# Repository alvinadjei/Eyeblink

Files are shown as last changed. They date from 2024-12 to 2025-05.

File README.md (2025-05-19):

# Eyeblink Experiment

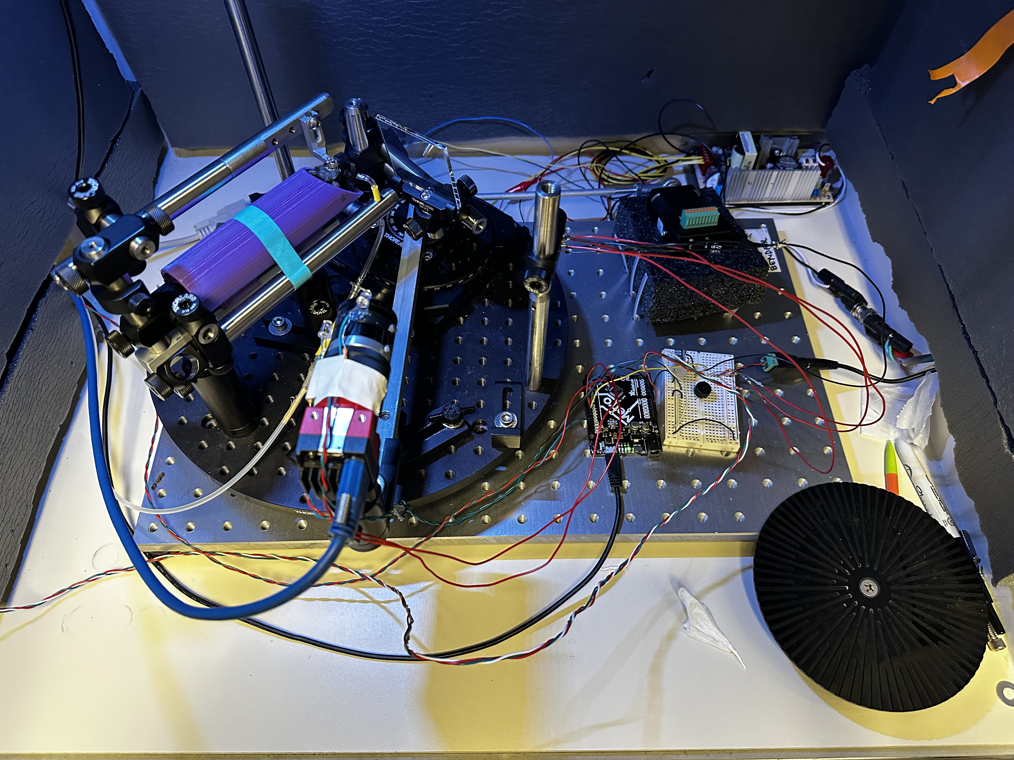
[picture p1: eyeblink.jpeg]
Eyeblink setup


This repository contains code and instructions for setting up an eyeblink conditioning experiment in mice. In this case, the conditioned stimulus is a short musical tone, 
and the unconditioned stimulus is a short puff of air to the mouse's eye. An infrared camera records a live feed of the mouse's eye, sending each frame to a Python script
that calculates how open or closed the mouse's eye is every millisecond.

This page is a work in progress, and will be updated as the project progresses.

Author(s): Alvin Adjei, University of California San Francisco

## Requirements
### Hardware
- Designed to work on Windows 10 and newer. Untested on Mac.
- 1 $\times$
  <a href="https://store.arduino.cc/products/arduino-uno-rev3?srsltid=AfmBOophdIvm8RfX5799wr4zovlr1sxV1jH-H7QClWuCym0v6gZN2AgC">
    Arduino Uno
  </a>
  or similar microcontroller (we used an <a href="https://www.adafruit.com/product/2488">Adafruit Metro Board</a>)
- 1 $\times$ Picospritzer III or similar device that can accept Arduino HIGH as input signal and outputs an air puff
- 1 $\times$
  <a href="https://www.adafruit.com/product/1426">
    neopixel strip
  </a>
- 5 $\times$ infrared LEDs (the ones we used emit light w/ 850nm wavelength)
- 5 $\times$ 220 $\Omega$ resistors
- 1 $\times$ N-Channel MOSFET
- 1 $\times$ passive piezoeelectric buzzer
- 1 $\times$
  <a href="https://www.edmundoptics.com/p/allied-vision-alvium-1800-u-120m-13-12mp-c-mount-usb-31-monochrome-camera/48262/">
    Allied Vision Alvium 1800 U-120m Monochrome Camera</a>,
  or similar camera with ___no___ infrared filter and compatible lens (in this case, for a 1/3" sensor)
  - Camera drivers and software are <a href="https://www.alliedvision.com/en/products/software/" target="_blank">here</a>
  - Python API manual is <a href="https://docs.alliedvision.com/Vimba_X/Vimba_X_DeveloperGuide/pythonAPIManual.html">here</a>
- 1 $\times$ <a href="https://www.edmundoptics.com/p/m6-and--20-mounting-plate-for-alvium/42353/">M6 and ¼-20 Mounting Plate for Alvium</a>
- 1 $\times$ Infrared mirror
- Other materials shown in the image at the top come from Thorlabs

### Software
The code for this project is written in Python and in the Arduino IDE. The required Python libraries and their versions are specified in <code>requirements.txt</code>.
To install them, run <code>python -m pip install -r requirements.txt</code>
in the terminal in the project's root directory.

The Arduino code requires the Adafruit NeoPixel library, which can be installed via the Library Manager in the Arduino IDE.

To interface with the camera, install the <a href="https://www.alliedvision.com/en/products/software/vimba-x-sdk/">Vimba X SDK</a> and the
<a href="https://docs.alliedvision.com/Vimba_X/Vimba_X_DeveloperGuide/about.html#installation">USB driver</a>. Then,
follow the instructions found <a href="https://docs.alliedvision.com/Vimba_X/Vimba_X_DeveloperGuide/pythonAPIManual.html">here</a> to install
Vimba X's Python API, VmbPy.

## Assembly
<figure>
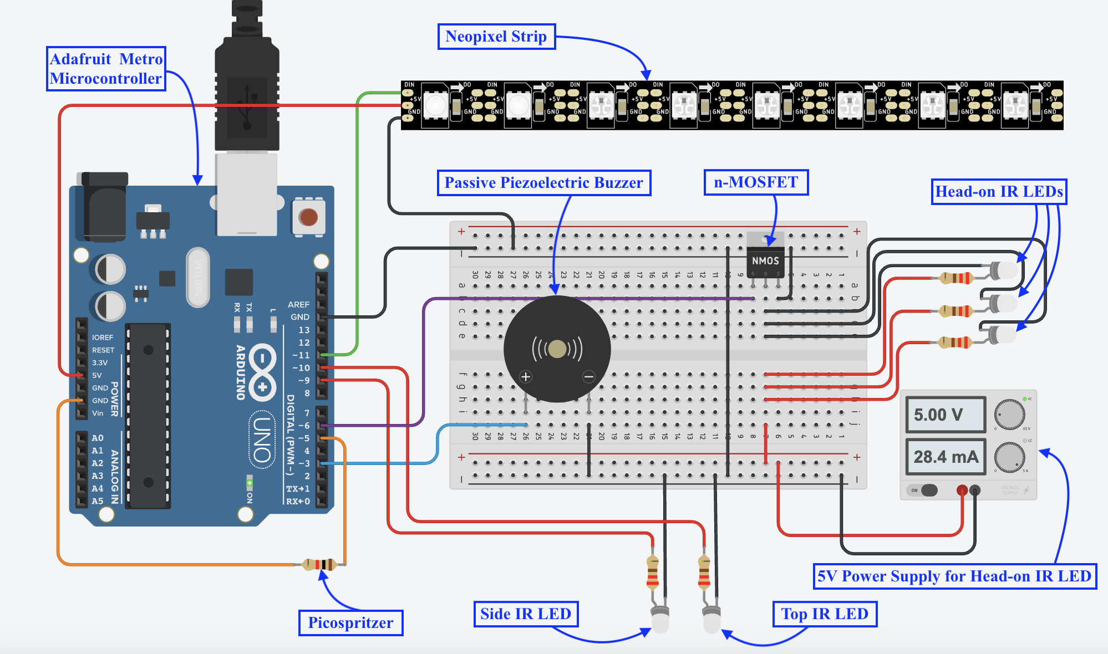
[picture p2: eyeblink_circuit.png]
Circuit Diagram
  
  <figcaption>
    Circuit diagram.
    <p>
      <b>Note: The Adafruit NeoPixel library uses pin 11 as the default data output pin for Neopixels on Arduino boards. If using an Adafruit Metro board like we did, pin 6 is the default data output pin for the Neopixels. Make sure your circuit and code align with the board you are using by appropriately setting the <i>PIX_PIN</i> and <i>IR_LED_3</i> variables in <code>Code/capture/Arduino/serial_control/serial_control.ino</code> according to your hardware.
      </b>
    </p>
    <p>
      The resistor in the bottom left represents the Picospritzer. The "Side IR LED" and "Top IR LED" are attached
      to the left and top of the camera. The "Head-on IR LEDS" are attached to a post facing the mouse head-on.
    </p>
  </figcaption>
</figure>

## Run Experiment

<ol>
  <li>Clone or download this repository.</li>
  <li>Plug USB camera and Arduino Uno into USB ports in the computer. The camera needs to be plugged into a USB 3 port, which is usually identified by having the color blue on the inside.</li>
  <li> Open <code>Code/capture/Arduino/serial_control/serial_control.ino</code>. This file contains instructions for the Arduino to execute when it receives serial instructions. Here, you can adjust constants like <code>csDuration</code> (how long the tone plays), <code>ISI</code> (inter-stimulus interval), and <code>usDuration</code> (how long the airpuff lasts) to your liking. Then, upload the code to the Arduino.</li>
  <li>Open <code>Code/capture/run_experiment.py</code></li>
  <li>Open the Device Manager on Windows to determine which USB port the camera is plugged into (e.g. 'COM4'), and set the <code>arduino_port</code>
  variable equal to this name (we have set this variable to <code>'COM4'</code> by default)</li>
  <li>
    Adjust global constants like <code>num_trials</code> (number of trials in an experiment) and <code>ITI</code> (inter-trial interval)
    to your liking.
  </li>
  <li>Navigate to the root directory of this project in the terminal, activate the <code>.venv-wind</code> virtual environment, then press the run button in your code editor to run the script.</li>
  <li>In the terminal, you will be prompted to enter the mouse's ID. Enter an ID of your choice and press Enter.</li>
  <li>Next, you will be asked if this is the first recording of the day for this mouse. If you enter 'y' for yes, you will continue to the next steps where you can run the experiment for <code>num_trials</code> iterations. If you enter 'n' for no, you will then be asked how many trials you would like to run on the mouse. Once you enter this, the following steps will be the same.</li>
  <li>
    Now, the GUI will open. If the window doesn't appear, check the app taskbar/dock for a new app running. The window should look something like this:
    <p>
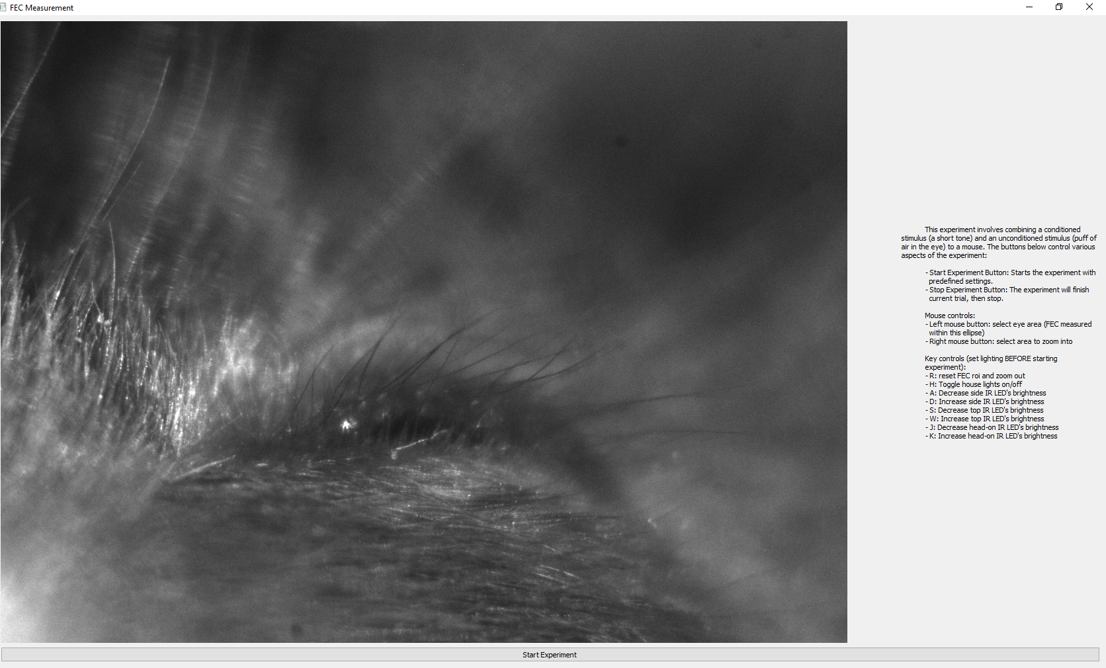
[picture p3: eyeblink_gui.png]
Eyeblink gui
      
    </p>
    <p>
      On the left, you should see a live video feed from the USB camera. On the right, there are instructions on how to adjust the brightness of the
    infrared LEDs, zoom in to the image, and select the region of interest (ROI) containing the mouse's eye. Once an ROI has been selected, click 
    "Start Experiment" at the bottom to begin data acquisition.
    </p>
  </li>
  <li>
    The experiment will run for the number of trials that you specified in <code>num_trials</code>. At any point, click the "Stop Experiment" button to
  terminate the experiment. If you terminate early, the data from the experiment up to that point will still be saved to CSV files.
  </li>
  <li>
    When the experiment is over, the data will be saved to two CSV files in the <code>Data/</code> directory. Each file will have the timestamp when it was
    saved in its name. The CSV saved to <code>Data/FEC/{mouse_id}/</code> has three columns: "Timestamp", "Trial #", and "FEC". It contains the timestamp, trial number, and
    fraction of eye closure, or FEC, in each frame. The CSV saved to <code>Data/stim/{mouse_id}/</code> has three columns: "Trial #", "CS Timestamp", and "Airpuff" containing the timestamp
    at which each trial's conditioned stimulus (in our case, the tone that plays before the airpuff) begins and whether an unconditioned stimulus (air puff) was executed during that trial.
  </li>
</ol>

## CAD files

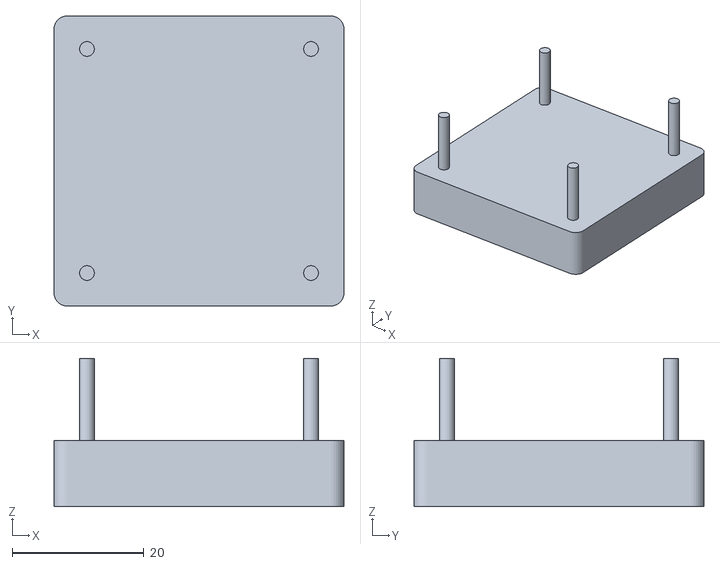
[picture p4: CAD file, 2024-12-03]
Camera Holder/ir_camera_holder.stl
44.0 x 44.0 x 22.5

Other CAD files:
Archived/Camera Holder/ir_camera_holder.f3d
Camera Holder/ir_camera_holder.f3d

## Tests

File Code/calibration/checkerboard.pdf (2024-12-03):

10/17/24, 2:56 PM | Checkerboard-A4-30mm-8x6.svg
file:///Users/alvinadjei/Desktop/UCSF/Bender Lab/VOR/Design/IR Camera/Checkerboard-A4-30mm-8x6.svg | 1/1

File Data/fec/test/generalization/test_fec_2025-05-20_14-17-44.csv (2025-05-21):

Timestamp | Trial # | FEC
2025-05-20 14:18:10.031412 | 1 | 0
2025-05-20 14:18:10.081845 | 1 | 0
2025-05-20 14:18:10.131754 | 1 | 0
2025-05-20 14:18:10.164043 | 1 | 0
2025-05-20 14:18:10.210908 | 1 | 0
2025-05-20 14:18:10.257772 | 1 | 0
2025-05-20 14:18:10.304635 | 1 | 0
2025-05-20 14:18:10.335880 | 1 | 0
2025-05-20 14:18:10.390175 | 1 | 0
2025-05-20 14:18:10.437007 | 1 | 0
2025-05-20 14:18:10.468280 | 1 | 0
2025-05-20 14:18:10.515151 | 1 | 0
2025-05-20 14:18:10.562011 | 1 | 0
2025-05-20 14:18:10.597852 | 1 | 0
2025-05-20 14:18:10.644746 | 1 | 0
2025-05-20 14:18:10.691609 | 1 | 0
2025-05-20 14:18:10.738475 | 1 | 0
2025-05-20 14:18:10.785309 | 1 | 0
2025-05-20 14:18:10.816591 | 1 | 0
2025-05-20 14:18:10.875238 | 1 | 0
2025-05-20 14:18:10.919471 | 1 | 0
2025-05-20 14:18:10.961386 | 1 | 0
2025-05-20 14:18:11.007236 | 1 | 0
2025-05-20 14:18:11.050125 | 1 | 0
2025-05-20 14:18:11.093006 | 1 | 0
2025-05-20 14:18:11.137887 | 1 | 0
2025-05-20 14:18:11.180771 | 1 | 0
2025-05-20 14:18:11.220816 | 1 | 0
2025-05-20 14:18:11.267677 | 1 | 0
2025-05-20 14:18:11.298896 | 1 | 0
2025-05-20 14:18:11.349378 | 1 | 0
2025-05-20 14:18:11.399887 | 1 | 0
2025-05-20 14:18:11.433147 | 1 | 0
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

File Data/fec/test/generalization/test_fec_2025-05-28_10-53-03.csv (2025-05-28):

Timestamp | Trial # | FEC
2025-05-28 10:57:31.168501 | 1 | 0
2025-05-28 10:57:31.198435 | 1 | 0
2025-05-28 10:57:31.248202 | 1 | 0
2025-05-28 10:57:31.295067 | 1 | 0
2025-05-28 10:57:31.341963 | 1 | 0
2025-05-28 10:57:31.373202 | 1 | 0
2025-05-28 10:57:31.420069 | 1 | 0
2025-05-28 10:57:31.466932 | 1 | 0
2025-05-28 10:57:31.513768 | 1 | 0
2025-05-28 10:57:31.560630 | 1 | 0
2025-05-28 10:57:31.591901 | 1 | 0
2025-05-28 10:57:31.641271 | 1 | 0
2025-05-28 10:57:31.691502 | 1 | 0
2025-05-28 10:57:31.730806 | 1 | 0
2025-05-28 10:57:31.780979 | 1 | 0
2025-05-28 10:57:31.814050 | 1 | 0
2025-05-28 10:57:31.866011 | 1 | 0
2025-05-28 10:57:31.911924 | 1 | 0
2025-05-28 10:57:31.947882 | 1 | 0
2025-05-28 10:57:31.994743 | 1 | 0
2025-05-28 10:57:32.041638 | 1 | 0
2025-05-28 10:57:32.072879 | 1 | 0
2025-05-28 10:57:32.119743 | 1 | 0
2025-05-28 10:57:32.166578 | 1 | 0
2025-05-28 10:57:32.213445 | 1 | 0
2025-05-28 10:57:32.260306 | 1 | 0
2025-05-28 10:57:32.291577 | 1 | 0
2025-05-28 10:57:32.349174 | 1 | 0
2025-05-28 10:57:32.381305 | 1 | 0
2025-05-28 10:57:32.431035 | 1 | 0
2025-05-28 10:57:32.480002 | 1 | 0
2025-05-28 10:57:32.514630 | 1 | 0
2025-05-28 10:57:32.564548 | 1 | 0
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

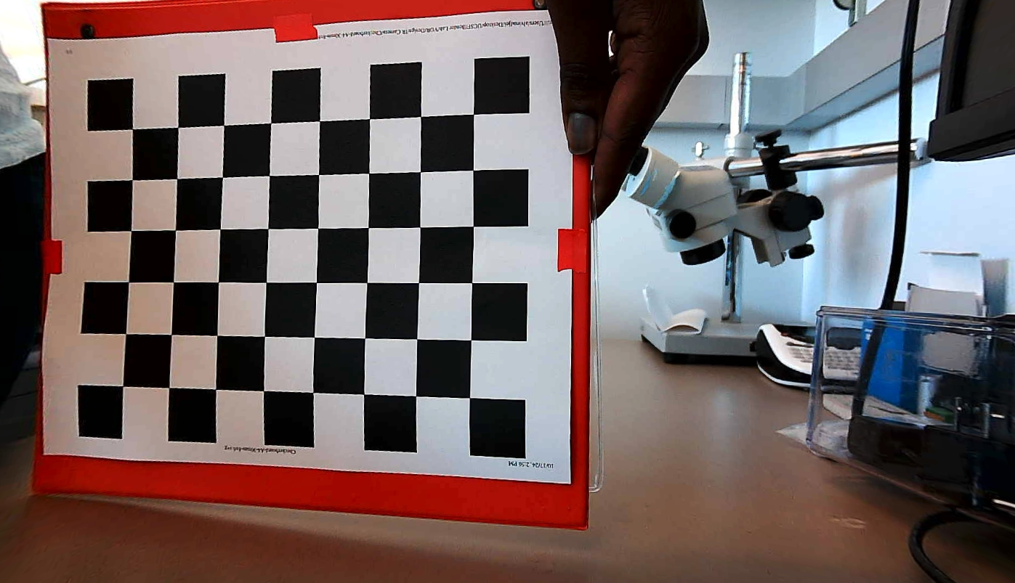
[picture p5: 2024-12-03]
Code/calibration/undistorted/calib_left12.png

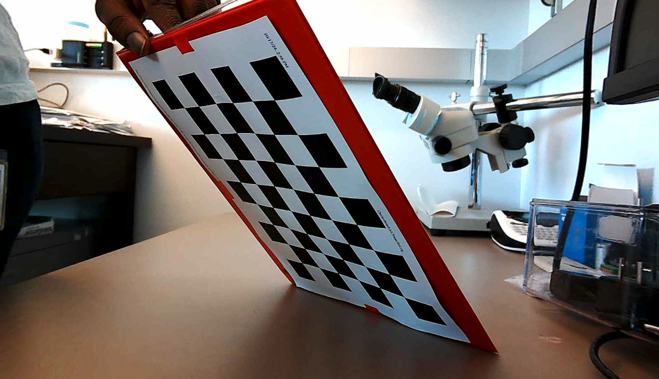
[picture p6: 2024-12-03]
Code/calibration/undistorted/calib_left10.png

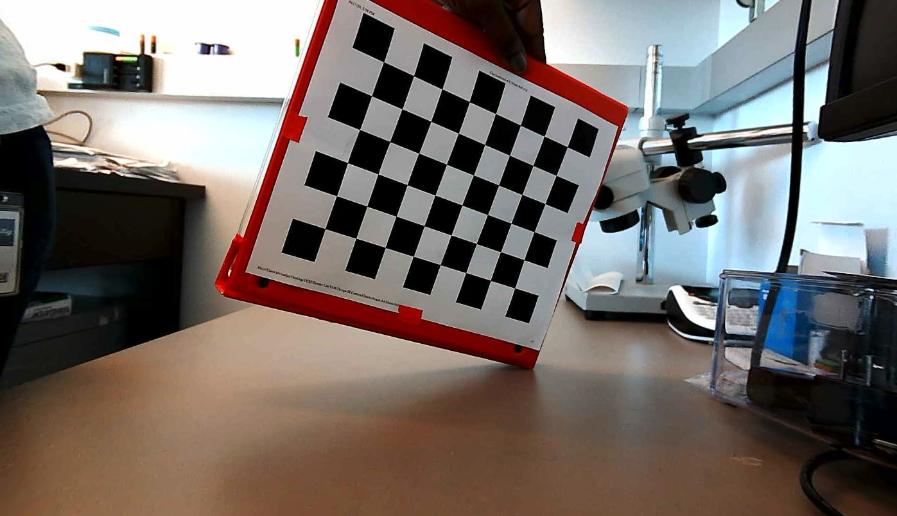
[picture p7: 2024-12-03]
Code/calibration/undistorted/calib_left05.png

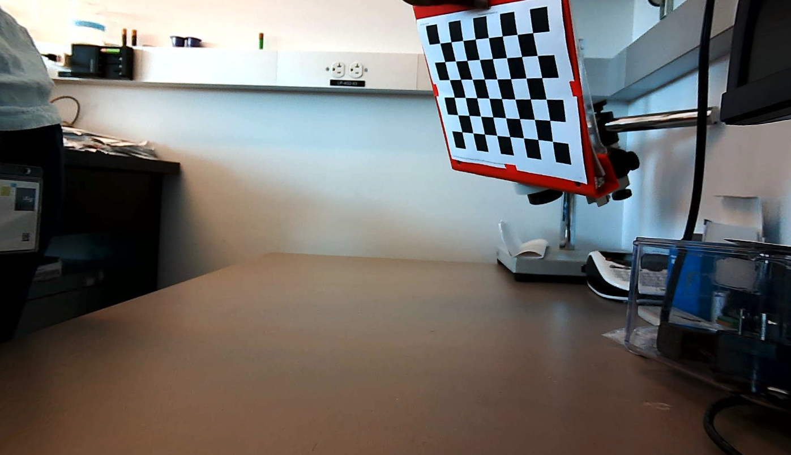
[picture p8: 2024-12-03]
Code/calibration/undistorted/calib_left01.png

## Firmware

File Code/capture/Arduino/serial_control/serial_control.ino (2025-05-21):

#include <Adafruit_NeoPixel.h>

#define BUZZER_PIN 3 // Buzzer control pin
#define PUFF_PIN 5 // Airpuff control pin
#define PIX_PIN 6 // Neopixel control pin
#define PIX_COUNT 8 // Number of NeoPixels
#define IR_LED_1 9 // Side IR LED control pin
#define IR_LED_2 10 // Top IR LED control pin
#define IR_LED_3 11 // Head-on IR LED control pin

// Define constants
int csDuration = 350; // 350 ms duration for CS
int ISI = 300; // 300 ms b/w CS onset and US onset
int usDuration = 50; // 50 ms duration for US

// Initialize Neopixel strip
Adafruit_NeoPixel strip(PIX_COUNT, PIX_PIN);

// Define NeoPixel white light color
uint32_t white = strip.Color(255, 255, 255);

// Define starting LED brightnesses
int brightness_1 = 255; // Side IR LED
int brightness_2 = 255; // Top IR LED
int brightness_3 = 255; // Head-on IR LED

// Default buzzer frequency
int freq;

// Keep track of whether neopixels are on or off
bool pixOn = true;

void setup() {
  // Setup neopixel strip
  strip.begin();
  strip.show(); // Initialize all pixels to 'off'
  
  // Initialize control pins
  pinMode(BUZZER_PIN, OUTPUT); // Buzzer
  pinMode(PUFF_PIN, OUTPUT); // Air puff

  // Initialize serial communication
  Serial.begin(9600);
}

void loop() {

  // Write brightness values to IR LED control pins
  analogWrite(IR_LED_1, brightness_1); // side
  analogWrite(IR_LED_2, brightness_2); // top
  analogWrite(IR_LED_3, brightness_3); // head-on

  // Turn overhead light on/off depending on value of pixOn
  if (pixOn) { // switch pixels on
        strip.fill(white); // Turn all pixels white
        strip.show(); // Push data to NeoPixel
        
      } else { // switch pixels off
        // Turn off all pixels
        strip.clear();
        strip.show();
      }
  
  if (Serial.available() > 0) {
    char command = Serial.read();
    
    // Command to toggle houselight
    if (command == 'h') { 
      pixOn = !pixOn; // toggle pixOn bool
      if (pixOn) {
        Serial.println("on");
      } else {
        Serial.println("off");
      }
    }

    // Command to turn down side IR brightness
    if (command == 'a') { 
      if (brightness_1 > 0) {
        brightness_1 -= 5;
        Serial.println(brightness_1);
      } else {
        Serial.println(-1);
      }
    }

    // Command to turn up side IR brightness
    if (command == 'd') { 
      if (brightness_1 < 255) {
        brightness_1 += 5;
        Serial.println(brightness_1);
      } else {
        Serial.println(-1);
      }
    }

    // Command to turn down top IR brightness
    if (command == 's') { 
      if (brightness_2 > 0) {
        brightness_2 -= 5;
        Serial.println(brightness_2);
      } else {
        Serial.println(-1);
      }
    }

    // Command to turn up top IR brightness
    if (command == 'w') { 
      if (brightness_2 < 255) {
        brightness_2 += 5;
        Serial.println(brightness_2);
      } else {
        Serial.println(-1);
      }
    }

    // Command to turn down head-on IR brightness
    if (command == 'j') { 
      if (brightness_3 > 0) {
        brightness_3 -= 5;
        Serial.println(brightness_3);
      } else {
        Serial.println(-1);
      }
    }

    // Command to turn up head-on IR brightness
    if (command == 'k') { 
      if (brightness_3 < 255) {
        brightness_3 += 5;
        Serial.println(brightness_3);
      } else {
        Serial.println(-1);
      }
    }

    // Command to run trial
    if (command == 'T' || command == 'F') {
      // Conditioned stimulus
      if (command == 'F') {
        // Wait for the rest of the int to arrive
        freq = Serial.parseInt(SKIP_NONE, 'F') * 1000;  // Reads the number after 'F'
      } else {
        freq = 10000;
      }

      // Begin CS-US
      Serial.println("d");
      tone(BUZZER_PIN, freq);
      
      delay(ISI); // Wait for ISI before starting US

      // If command is 'F', don't do airpuff
      if (command == 'T') {
        // Unconditioned stimulus
        digitalWrite(PUFF_PIN, HIGH); // Start airpuff
        delay(usDuration); // Duration of the air puff
        digitalWrite(PUFF_PIN, LOW);
      } else { // no airpuff
        delay(usDuration); // Duration of the air puff
      }

      delay(csDuration - ISI - usDuration); // Finish playing tone
      noTone(BUZZER_PIN);
    }
  }
}

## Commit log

2024-12-03 Created repo
    [ir_camera_holder.f3d, ir_camera_holder.stl, mouse_0_fec.csv, mouse_0_stim.csv]
2024-12-04 Transitioned to windows
    Need to fix camera feed dimensions and coordinates, acting funky
    [mouse_0_fec.csv, mouse_0_stim.csv]
2024-12-04 Fixed cv2 window
    Image gets laggy at the beginning of each trial when bulk of threading is happening, need to explore multiprocessing option to see if that helps
    [ir_camera_holder.f3d, ir_camera_holder.stl, mouse_0_fec.csv, mouse_0_stim.csv]
2024-12-09 Saved working threading code
2024-12-09 Fixed threading file location
2024-12-09 Arduino code for ir leds
2025-01-02 Added multiprocessing to mitigate camera lag
2025-01-03 Removed multiprocessing, all threading
2025-01-03 Threading and QThread implementation
2025-01-04 Software implementation is basically done
    Will go through later to clean up
    [mouse_0_fec.csv, mouse_0_stim.csv]
2025-01-06 Rearranged files and added LED controls
    [mouse_0_fec.csv, mouse_0_stim.csv]
2025-01-06 Fixed text spacing and bug in stop_experiment
    [mouse_0_fec.csv, mouse_0_stim.csv]
2025-01-07 Fixed 0% IR LED brightness bug
2025-01-14 Implemented piezo buzzer for CS
    stim csv's now only save CS onset timestamp, since US timing now happens completely within arduino
    [mouse_0_fec.csv, mouse_0_stim.csv]
2025-01-21 Changed csv saving
    [mouse_0_fec.csv, mouse_0_fec_2025-01-21_11-10-48.csv, mouse_0_stim.csv, mouse_0_stim2025-01-21_11-10-48.csv]
2025-01-31 Rearranged files
    [ir_camera_holder.f3d, ir_camera_holder.stl, mouse_0_fec_2025-01-21_11-10-48.csv, mouse_0_stim2025-01-21_11-10-48.csv]
2025-01-31 Added Camera user manual
2025-02-04 Added eyeblink circuit picture
2025-02-04 Update README.md
    Added circuit diagram and alt text for images
2025-02-20 Start implementing camera code
2025-02-21 Connected new camera to python script
2025-02-21 Allow loading of camera settings
2025-02-25 Updated camera settings and neopixel brightness
2025-02-26 Update README.md
    Clarified the quirks of the default output pin for the Arduino's Neopixel library and how it differs b/w the Arduino Uno and the Adafruit Metro microcontrollers
2025-02-26 Eyeblink circuit image edits
2025-03-03 Update README.md
    Added transistor to materials
2025-03-03 Update README.md
    Edited circuit diagram caption
2025-03-03 Update README.md
    Add camera mount to materials
2025-03-04 Updated circuit again (hopefully last time)
2025-03-06 Mounted camera, fixed 'h' serial command
2025-03-14 Moved data saving to stop_experiment
    FEC data saving correctly, stim data is not triggering conditional to save correctly
    Need to fix camera errors when closing the window
    [mouse_0_fec_2025-03-14_15-47-01.csv, mouse_0_fec_2025-03-14_15-49-59.csv]
2025-03-17 Replaced gui image
    [mouse_0_fec_2025-03-17_14-34-54.csv, mouse_0_fec_2025-03-17_15-23-28.csv, mouse_0_fec_2025-03-17_15-24-24.csv, mouse_0_stim_2025-03-17_15-24-24.csv]
2025-03-17 Adjust binary threshold
    [mouse_0_fec_2025-03-17_15-41-08.csv]
2025-03-19 Fixed data saving bug
    [mouse_0_fec_2025-03-14_15-47-01.csv, mouse_0_fec_2025-03-14_15-49-59.csv, mouse_0_fec_2025-03-17_14-34-54.csv, mouse_0_fec_2025-03-17_15-23-28.csv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]
2025-03-19 Update stim_data by concat instead of replacement
    [mouse_0_fec_2025-03-19_12-50-40.csv, mouse_0_stim_2025-03-19_12-50-40.csv]
2025-04-21 Collect data to build processing pipeline
    [mouse_0_fec_2025-04-21_11-21-51.csv, mouse_0_stim_2025-04-21_11-21-51.csv]
2025-04-21 Added random airpuff dropout logic to arduino
    Tested data saving, everything is working
    [mouse_0_fec_2025-04-21_11-21-51.csv, mouse_0_fec_2025-04-21_14-20-04.csv, mouse_0_stim_2025-04-21_11-21-51.csv, mouse_0_stim_2025-04-21_14-20-04.csv]
2025-05-07 Fixed early experiment termination bug
    [mouse_8689S_fec_2025-05-07_15-47-28.csv, mouse_8689S_stim_2025-05-07_15-47-28.csv]
2025-05-09 Data collection 5/8/2025
    [mouse_6599TR_fec_2025-05-08_15-37-57.csv, mouse_6599TR_stim_2025-05-08_15-37-57.csv, mouse_8689S_fec_2025-05-08_17-29-17.csv, mouse_8689S_stim_2025-05-08_17-29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]
2025-05-12 Data collection 5/10-5/11
    [0_fec_2025-05-09_11-12-12.csv, 0_fec_2025-05-09_15-46-52.csv, 0_stim_2025-05-09_11-12-12.csv, 0_stim_2025-05-09_15-46-52.csv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]
2025-05-12 Save video along with data
    [test_fec_2025-05-12_14-07-55.csv, test_stim_2025-05-12_14-07-55.csv]
2025-05-13 Data collection 5/12
    [6599TR_fec_2025-05-12_14-46-19.csv, 6599TR_stim_2025-05-12_14-46-19.csv, 8689J_fec_2025-05-12_16-27-32.csv, 8689J_stim_2025-05-12_16-27-32.csv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]
2025-05-13 Collected data 6599TR 5/13
    [6599TR_fec_2025-05-13_10-54-43.csv, 6599TR_stim_2025-05-13_10-54-43.csv]
2025-05-13 8689 Cage Data Collection 5/13
    [8689J_fec_2025-05-13_15-53-16.csv, 8689J_stim_2025-05-13_15-53-16.csv, 8689S_fec_2025-05-13_13-54-54.csv, 8689S_stim_2025-05-13_13-54-54.csv]
2025-05-14 Data Collection 5/14
    [6599TR_fec_2025-05-14_10-39-44.csv, 6599TR_stim_2025-05-14_10-39-44.csv, 8689J_fec_2025-05-14_11-25-58.csv, 8689J_stim_2025-05-14_11-25-58.csv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]
2025-05-16 Data collection 5/15/25
    [6599TR_fec_2025-05-15_15-17-52.csv, 6599TR_stim_2025-05-15_15-17-52.csv, 8689J_fec_2025-05-15_14-12-48.csv, 8689J_fec_2025-05-15_16-17-05.csv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]
2025-05-16 Data collection 5/16/25
    [6599TR_fec_2025-05-16_15-42-29.csv, 6599TR_stim_2025-05-16_15-42-29.csv, 8689J_fec_2025-05-16_15-06-43.csv, 8689J_stim_2025-05-16_15-06-43.csv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]
2025-05-17 Data collection 5/17
    [6599TR_fec_2025-05-17_12-59-55.csv, 6599TR_stim_2025-05-17_12-59-55.csv, 8689J_fec_2025-05-17_12-22-31.csv, 8689J_stim_2025-05-17_12-22-31.csv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]
2025-05-19 Data acquisition 5/18
    [6599TR_fec_2025-05-18_17-32-17.csv, 6599TR_stim_2025-05-18_17-32-17.csv, 8689J_fec_2025-05-18_18-49-45.csv, 8689J_stim_2025-05-18_18-49-45.csv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]
2025-05-19 Data collection 5/19 8689J
    [8689J_fec_2025-05-19_13-13-20.csv, 8689J_stim_2025-05-19_13-13-20.csv]
2025-05-19 Data collection 5/19 (first generalization runs)
    [0_fec_2025-05-19_14-19-44.csv, 0_fec_2025-05-19_14-23-35.csv, 0_fec_2025-05-19_14-28-12.csv, 0_fec_2025-05-19_14-32-03.csv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]
2025-05-20 Data acquisition 5/19 8689S pt 2
    [8689S_fec_2025-05-19_19-31-04.csv, 8689S_stim_2025-05-19_19-31-04.csv]
2025-05-21 Fully implemented generalization; data 5/20
    Need to switch out buzzer for louder speaker with better range
    [0_fec_2025-05-09_11-12-12.csv, 0_fec_2025-05-09_15-46-52.csv, 0_fec_2025-05-19_14-19-44.csv, 0_fec_2025-05-19_14-23-35.csv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]
2025-05-21 Fixed misplaced data files
    [8689J_fec_2025-05-19_13-13-20.csv, 8689J_stim_2025-05-19_13-13-20.csv]
2025-05-22 Data collection 5/21
    [6599TR_fec_2025-05-21_14-20-42.csv, 6599TR_fec_2025-05-21_14-27-15.csv, 6599TR_stim_2025-05-21_14-20-42.csv, 6599TR_stim_2025-05-21_14-27-15.csv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]
2025-05-22 Data collection 5/22
    [6599TR_fec_2025-05-22_10-24-40.csv, 6599TR_stim_2025-05-22_10-24-40.csv, 8689J_fec_2025-05-22_11-58-03.csv, 8689J_stim_2025-05-22_11-58-03.csv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]
2025-05-23 Data collection 5/23
    [6599TR_fec_2025-05-23_11-05-55.csv, 6599TR_stim_2025-05-23_11-05-55.csv, 8689J_fec_2025-05-23_11-43-58.csv, 8689J_stim_2025-05-23_11-43-58.csv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]
2025-05-25 Data collection 5/24
    [6599TR_fec_2025-05-24_15-39-45.csv, 6599TR_stim_2025-05-24_15-39-45.csv, 8689J_fec_2025-05-24_17-10-29.csv, 8689J_stim_2025-05-24_17-10-29.csv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]
2025-05-26 Data collection 5/25
    [6599TR_fec_2025-05-25_14-44-17.csv, 6599TR_stim_2025-05-25_14-44-17.csv, 8689J_fec_2025-05-25_16-40-19.csv, 8689J_stim_2025-05-25_16-40-19.csv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]
2025-05-27 Data collection 5/26
    [6599TR_fec_2025-05-26_14-43-34.csv, 6599TR_stim_2025-05-26_14-43-34.csv, 8689J_fec_2025-05-26_16-36-24.csv, 8689J_stim_2025-05-26_16-36-24.csv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]
2025-05-27 Increased pre-CS onset time
    Start collecting timestamp and video data 500ms before CS onset (formerly 50 ms)
    Removed extraneous self.wait() call in stop() method of CameraThread class, need to see if this fixes window closing error
2025-05-28 Preliminary testing of flask site (working)
    [test_fec_2025-05-28_10-53-03.csv, test_stim_2025-05-28_10-53-03.csv]
2025-12-23 Added data analysis code
    Single and multiple mice across multiple days
    [8689S_stim_2025-05-09_13-49-16.csv, 8689S_stim_2025-05-11_20-33-29.csv, 8689S_stim_2025-05-11_20-57-29.csv, 8689S_stim_2025-05-12_15-34-40.csv]
2025-12-23 Crop camera feed (probably unnecessary)
